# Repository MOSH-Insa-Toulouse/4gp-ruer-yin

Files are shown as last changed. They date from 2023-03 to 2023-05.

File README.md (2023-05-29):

# 22-23 4gp-ruer-yin

Ce projet s'inscrit dans l'UF **"I4GPMH21 - du capteur au banc de test en open source hardware"** en 4eme année département d'INSA Toulouse.
***

Ce projet sert à caractériser la résistance des capteurs graphites sous différentes conditions de déformation. Une application de déformation change la distance moyenne des particules de graphite. En effet, la conductivité de la couche graphite dépende vachement de cette distance moyenne et donc la déformation. En pratique, on applique un contraint et déposer le capteur sur les semis sphères pour caractériser les diffèrent déformation. L’ordre de grandeur de ce capteur est 100Mohm. Il n’est pas usuel. Par exemple il est hors la gamme de mesure des multimètres commerciaux. Donc il est essentiel dans ce projet de planifier et de fabriquer un circuit PCB qu’il nous permettre de mesurer cette résistance. De plus, il est aussi intéressant d’élaborer un système de communication pour communiquer les données avec notre téléphone Android avec Bluetooth. 
***  
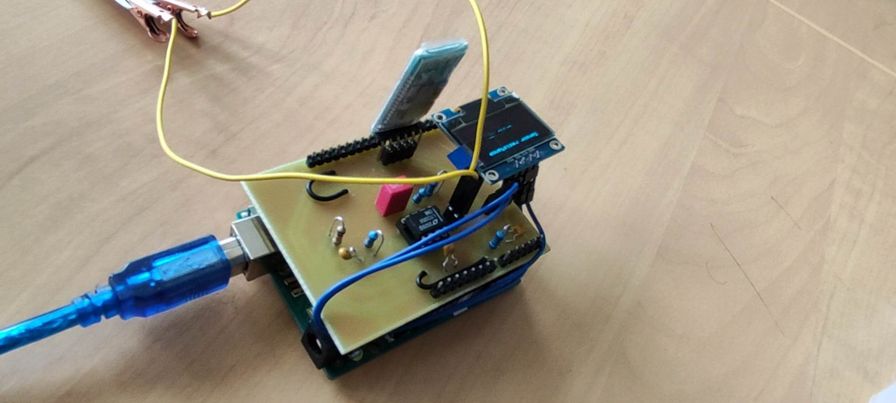
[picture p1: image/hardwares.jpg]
hardware

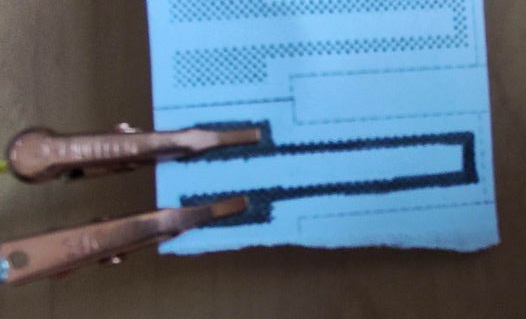
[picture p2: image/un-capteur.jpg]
capteur

## Table de matière
* [1. Liverables et matériels](#PremiereSection)
* [2. Simulation LTSPICE](#SixiemeSection)
* [3. Réalisation Kicad et PCB](#DeuxiemeSection)
* [4. Code Arduino](#TroisemeSection)
* [5. (Application MIT app inventor)](#QuartiemeSection)
* [6. (Banc de test)](#CinqiemeSection)
## 1. Liverables et matériels 
***
Les liverables principaux sont: 
* Un sheild PCB de module Arduino Uno au dessus on a intégré un circuit d'amplificateur, un OLED et un module Bluetooth.
* Un application Android exploré avec MIT app inventor. Cet app sert à communiquer en temp relle avec le module d'Arduino des valeurs de resistance et les afficher. 
* Un script d'Arduino permettant de calculer en temps relle du valeur de resistance, communiquer ce valeur avec l'application mentionné au dessus et l'afficher sur l'écran OLED
* Un datasheet contenant tous les caratérisation du capteur. 

Les matériels nécessaires sont:
* Un carte PCB de module Arduino Uno
* Un module Bluetooth HC-05
* Un écran OLED
* Un amplificateur opérationnel LTC1050  
* Deux condensateurs de 100 nF  
* Un condensateur de 100 µF 
* Deux résistances de 100 KOhms  
* Une résistance de 10 KOhms  
* Deux résistances de 1 KOhm  
* Un papier dessiné d'un trace de crayon imposé
## 2. Simulation LTSpice
La capteur graphite a une l'ordre de grandeur de 100MOhm. Le voltage maximun d'Arduino est 5V. Il est donc difficile de mesure la valeur de capteur si on n'arrive pas à amplifier la signal. On a donc designé un circuit d'amplification pour avoir un facteur 100 du signal. Ensuite on peut calculer le valeur précise de la résistance. Voici l'image du circuit de LTSpice:
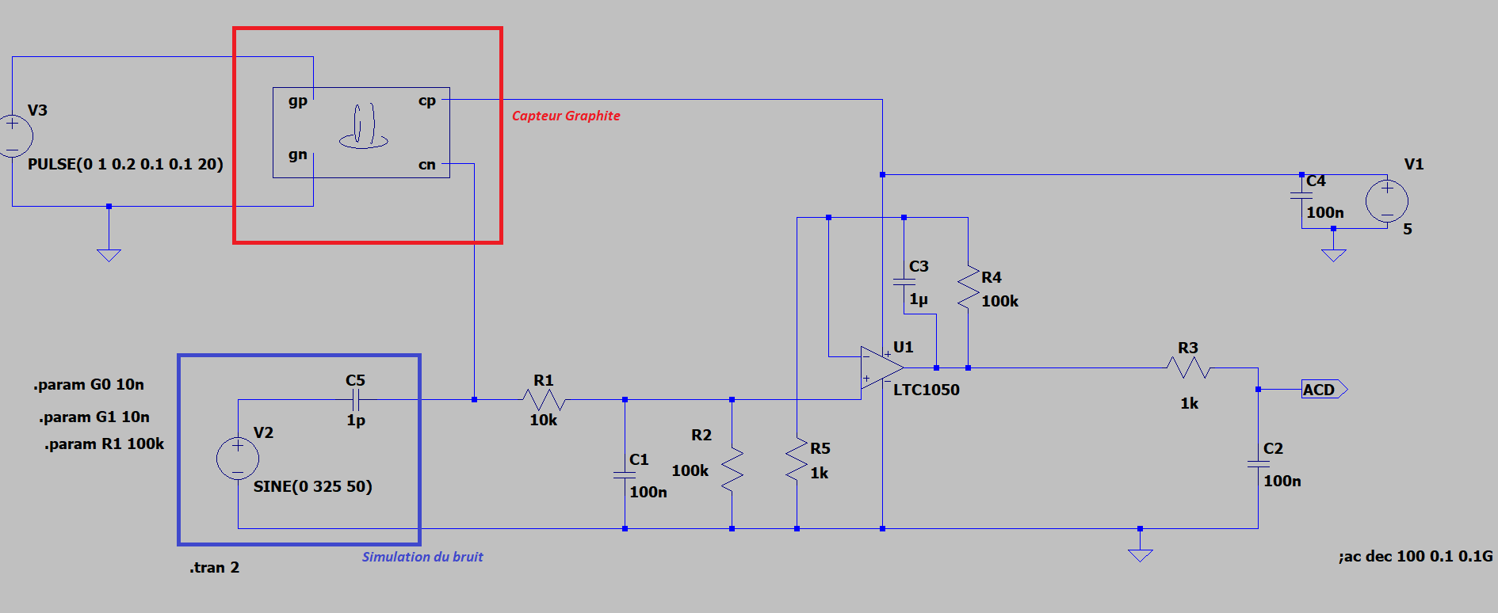
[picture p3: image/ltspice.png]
ltspice


## 3. Réalisation Kicad et PCB 
Pour designer un carte PCB où on peut intégrer les matériels mentionnés au dessus, il est nécessaire de utiliser kicad pour designer un circuit de conductant de cuivre et les composants soudés au dessus. Les détailes de ces composants et de la cirtuit sont visibles dans les images au dessous.  
* L'image des symboles:
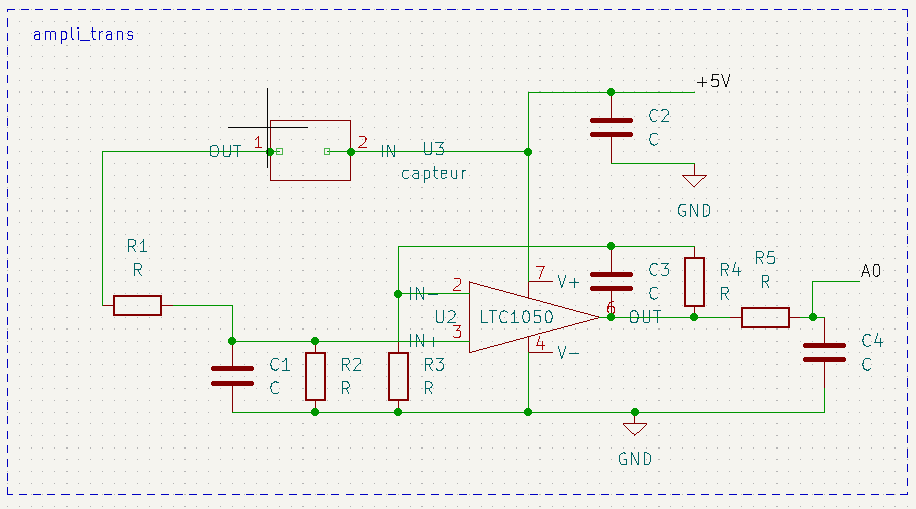
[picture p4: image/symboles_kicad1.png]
symbole1

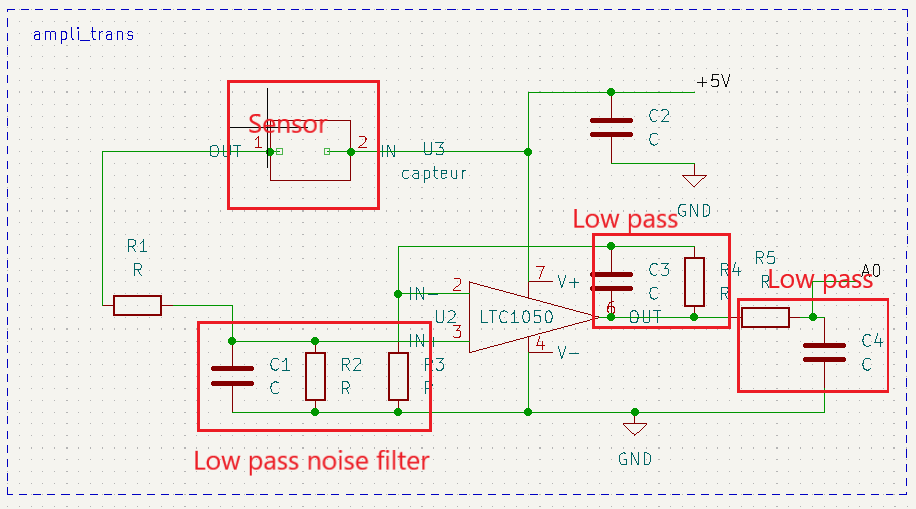
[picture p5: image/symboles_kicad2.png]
symbole2

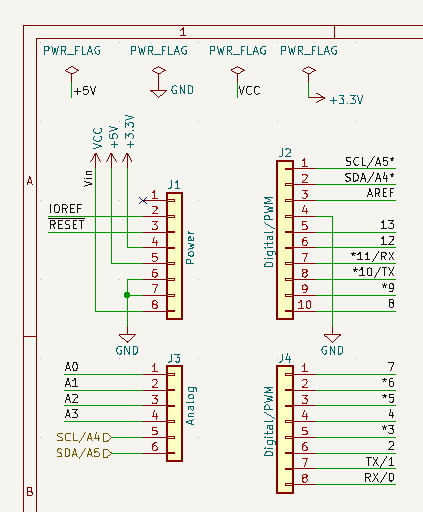
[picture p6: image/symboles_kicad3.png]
symbole3


* L'image du PCB et son image 3D
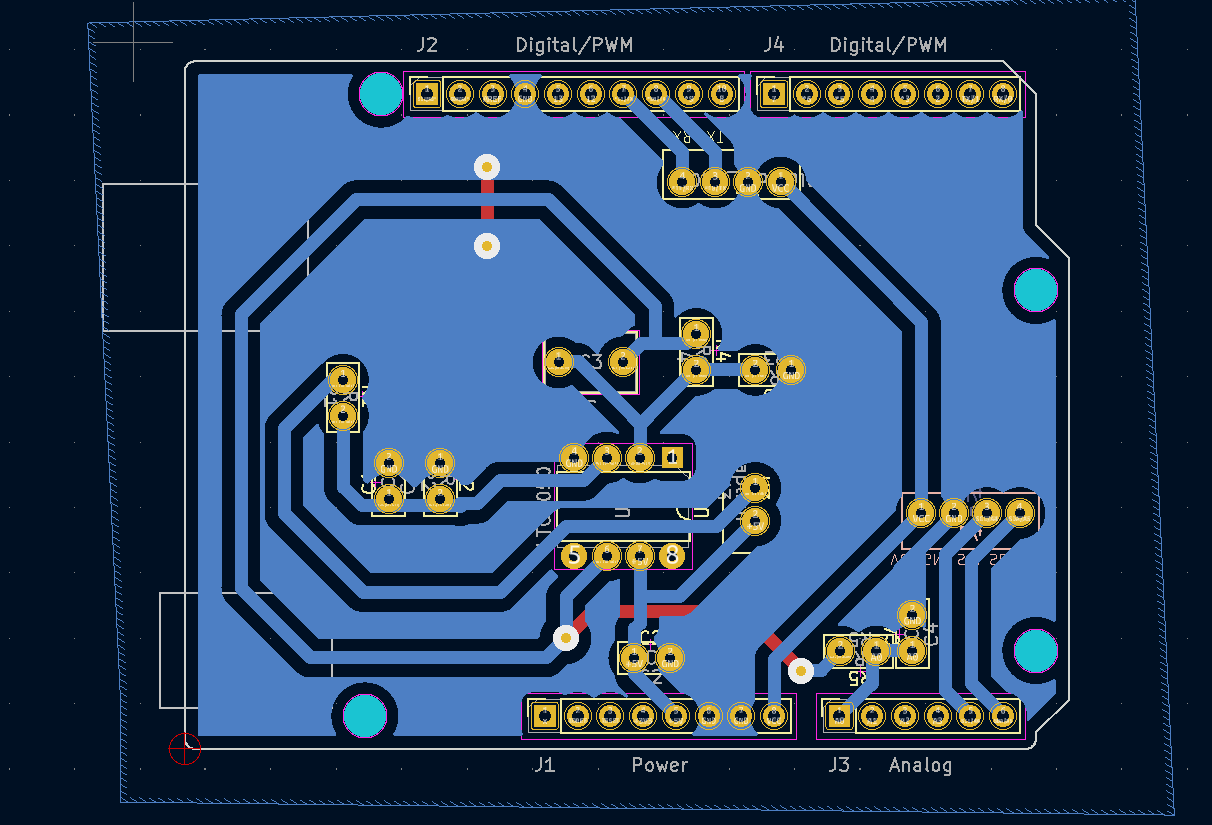
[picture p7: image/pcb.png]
pcb
 

Après les vérifications electroniques, nous avons envoyé le fichier d'imprimant à Madame Catherine Crouzet pour poursuivre un impression de PCB avec elle. Ce PCB est réalisé sur un plaquette epoxy. A la fin des procédés de photolitographie et de gravure chimique, l'impression du circuit est réalisé sur l'un de cette plaquette. Nous avons poursuive les perçages des trous pour intégrer les matériels et le soudage de ces matériels. Les trous on les 2 différents diamètres. Pour les trous du module Arduino Uno, le diametre est 1mm. Les trous de reste ont de diametre 0.8mm selon la consigne de Madame Catherine Crouzet.

## 4. Code Arduino 
Les objetifs de script d'arduino nommé [plz-work.ino](https://github.com/MOSH-Insa-Toulouse/4gp-ruer-yin/tree/main/Arduino/plz-work/plz-work) sont:
* mesurer le voltage en temp relle de la sortie du circuit (VA0)
* En déduire la valeur de résistance R du capteur graphite.
* Envoyer la valeur de tension mesuré sous 1 octect par le module de bluetooth.
* Afficher la valeur de résistance sur l'écran OLED.
Le code essentielle est effctivement les code de mesure et de calcule de valeur de résistance. Selon les simulations de LTSpice, on peut en deduit la resistance exact que nous aimerions de mesurer.

## 5. Application (MIT app inventor) 
Les objetifs de cet application est de communiquer en temp relle avec le module d'Arduino des valeurs de resistance et les afficher. 
La connection de bluetooth se réalise par trois bloc de "when". On affiche le liste d'adresse de bluetooth dans le mémoire de téléphone. Puis on pourra sélectionner un adresse. Le téléphone est ensuite connecté à bluetooth. 
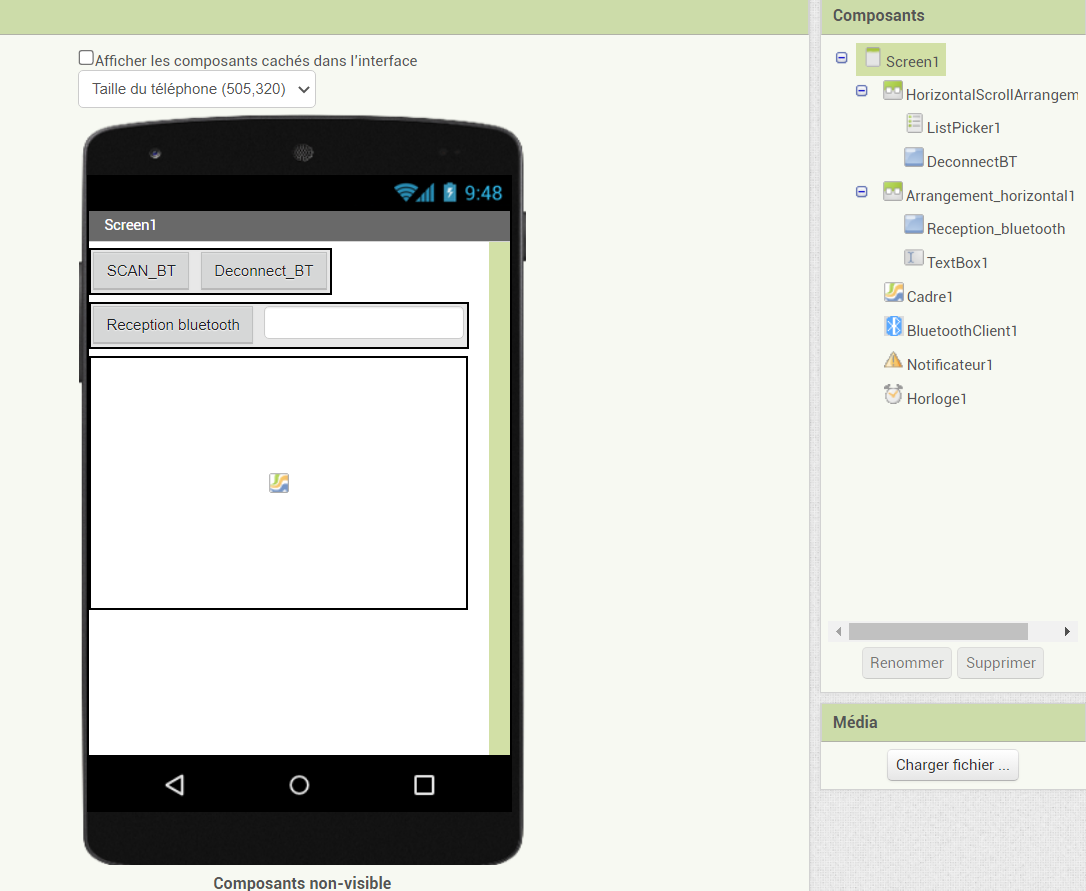
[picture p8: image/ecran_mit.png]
MIT


Le Bouton "Reception_bluetooth" sert à lancer le chronologe. Ensuite, l'application fait le calcule depuis un octet envoyé par le Bluetooth HC-05 en utilisant la simulation de LTspice. Dans le graphe, on trace le graphe en tracant tous les lignes entre tous les 2 point.   

## 6. Banc de test 
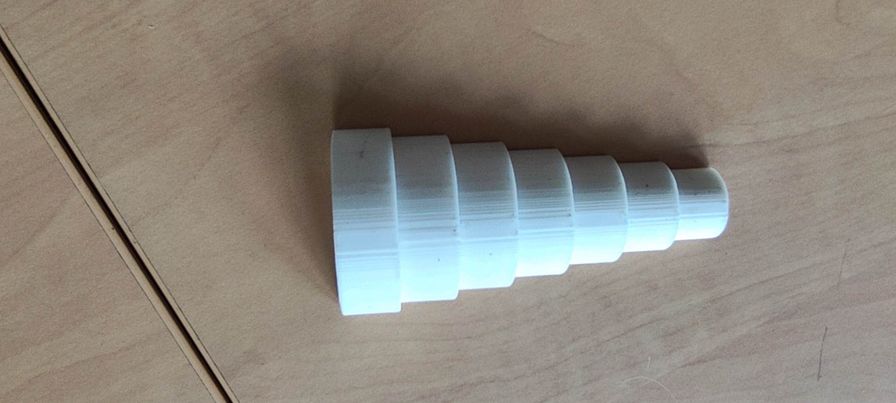
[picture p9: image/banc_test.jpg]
banc de test


Nous avons testé notre capteur graphite dans les différent angle de déformation. Ce dernier est caractériser par un banc de test dans l'image au dessus. Le banc de test est composé par les différents semi sphère de diamètre 5cm, 4.5cm, 4cm, 3.5cm, 3cm, 2.5cm, 2cm. Pendant le test, on colle le côté où il y a pas de graphite aux différent semi shère du banc de test et on fait le mesure du résistance. Ensuite on cherche la relation entre le déformation définit comme par le formule ε=D/(2*R)(où ε est la déformation, D est l'épaisseur du papier, R est la rayon de courbure) et la variation relative de (ΔR/R0).  
Nous avons décidé de faire les tests sur un graphite de 2H en applicant la seulement la tension. Il y a pas de mesure sous condition de compression car on a réalisé pendant les mesure que la forme de capteur graphite n'est pas réversible. Premièrement, on peut très facilement dépasser le limite élastique du papier. Deuxièmement, même si on ne change pas la forme de ce papier, la résistance n'est souvent pas réversible. En conséquence, on a choisit de faire le mesure seulment sur la tension pour chaque échantillon. Les résultat sont montré dans le fichier Datasheet.pdf.
Le résultat montre une relation linéaire entre la déformation et la variation relative de la résistance de capteur. On peut déduit l'angle de déformation  depuis un résistance mesurée. 

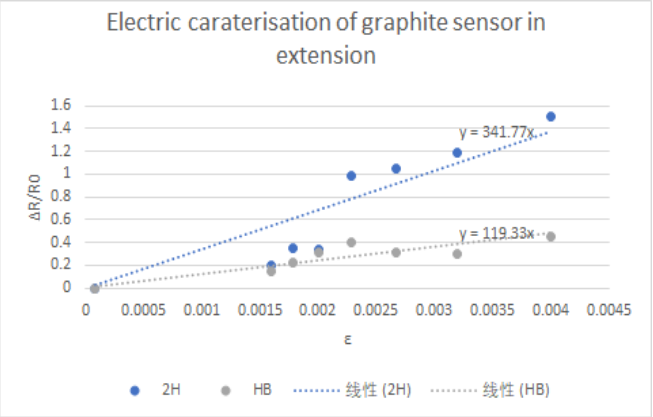
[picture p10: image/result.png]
result


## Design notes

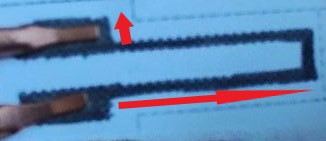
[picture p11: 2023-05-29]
image/344186423_743219774252609_5498657226306865498_o.jpg

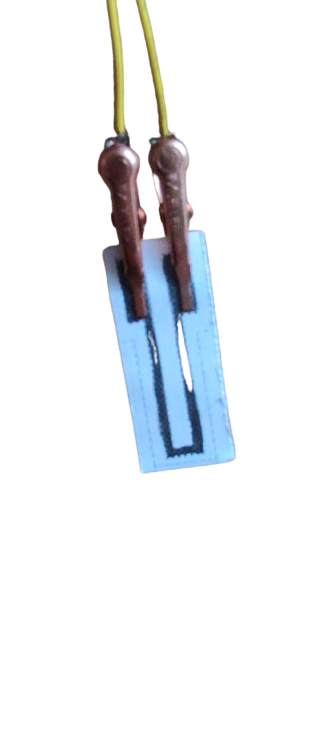
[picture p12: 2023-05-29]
image/344304782_1337325953871078_4266992527923061685_n-removebg-preview.png

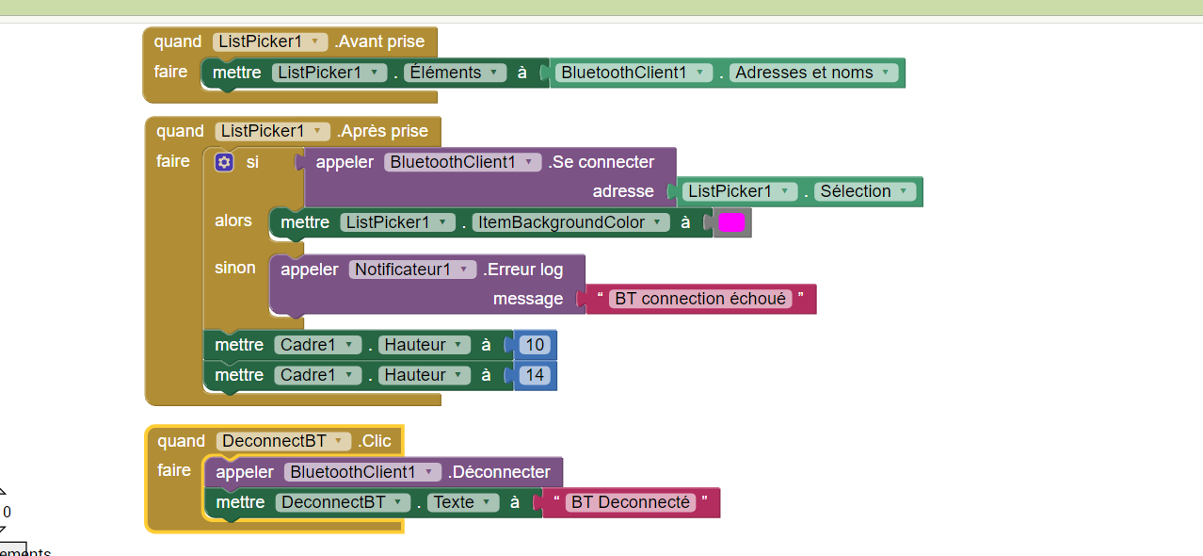
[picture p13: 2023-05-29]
image/MIT App Inventor 2 - Google Chrome 2023_5_11 22_43_18.png

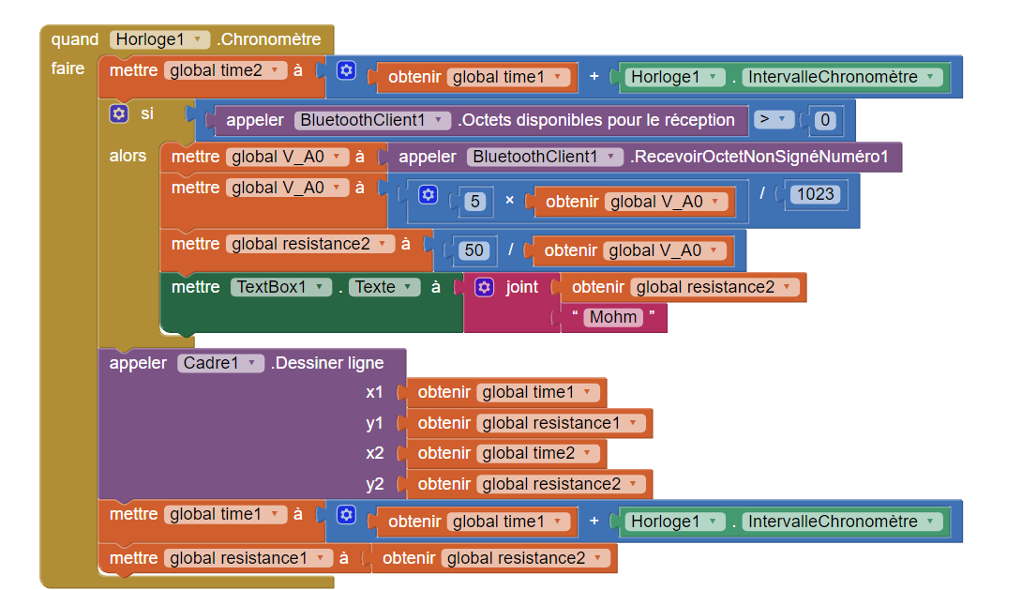
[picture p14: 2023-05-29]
image/MIT App Inventor 2 - Google Chrome 2023_5_12 16_00_10.png

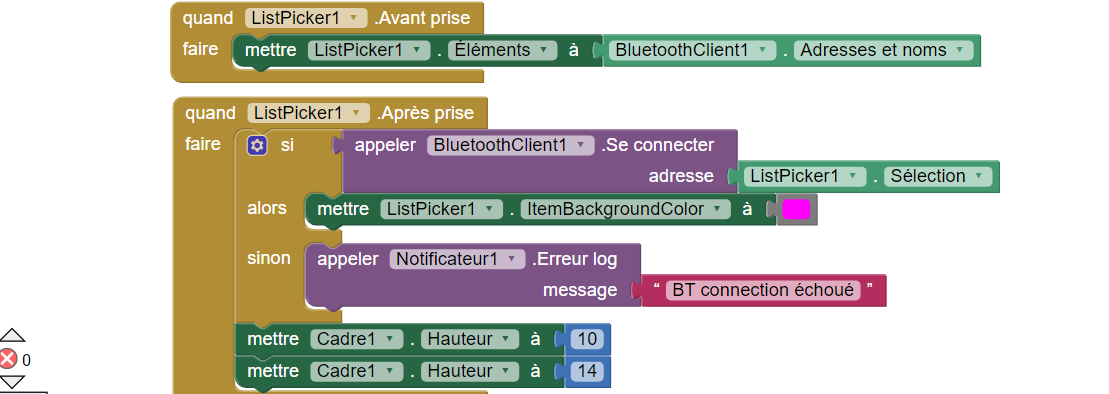
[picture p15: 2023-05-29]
image/MIT App Inventor 2 - Google Chrome 2023_5_11 22_40_17.png

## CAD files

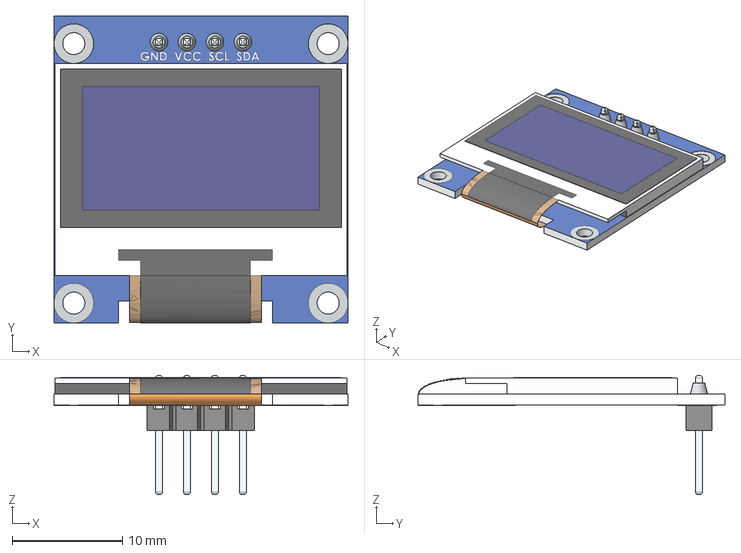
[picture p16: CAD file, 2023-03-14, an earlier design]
pcb_capteur_graphite_V2/mod3D/display-oled-ssd1306-de-0-96-1.snapshot.6/OLED-128x64-0.96.step
26.7 x 27.9 x 10.8 mm

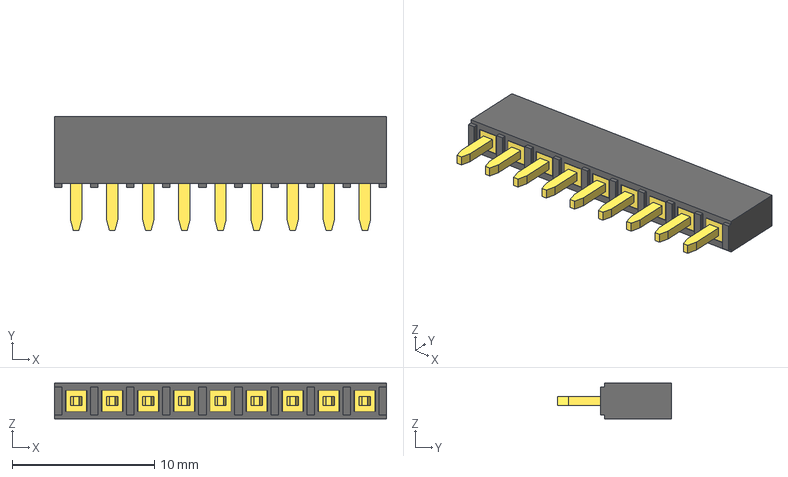
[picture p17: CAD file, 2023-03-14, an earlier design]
pcb_capteur_graphite_V2/mod3D/pin_header/9-Pin Header - Female - 2.54mm.step
23.4 x 8.00 x 2.50 mm

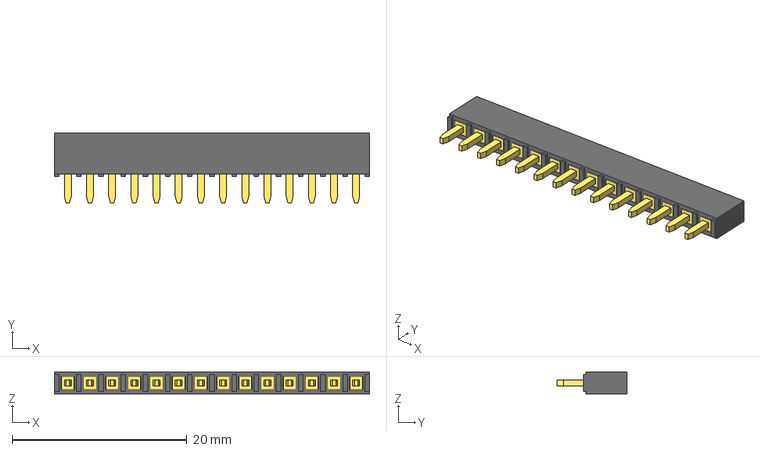
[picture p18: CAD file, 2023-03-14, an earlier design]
pcb_capteur_graphite_V2/mod3D/pin_header/14-Pin Header - Female - 2.54mm.step
36.1 x 8.00 x 2.50 mm

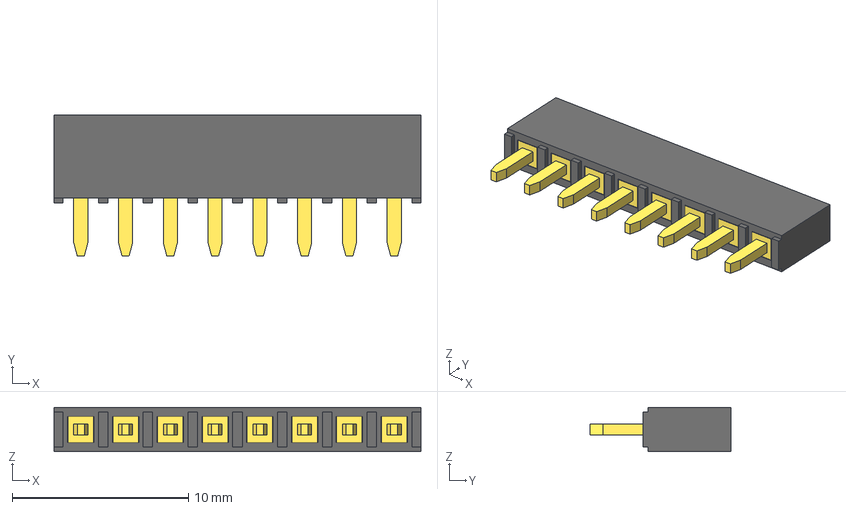
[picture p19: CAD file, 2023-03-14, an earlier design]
pcb_capteur_graphite_V2/mod3D/pin_header/8-Pin Header - Female - 2.54mm.step
20.8 x 8.00 x 2.50 mm

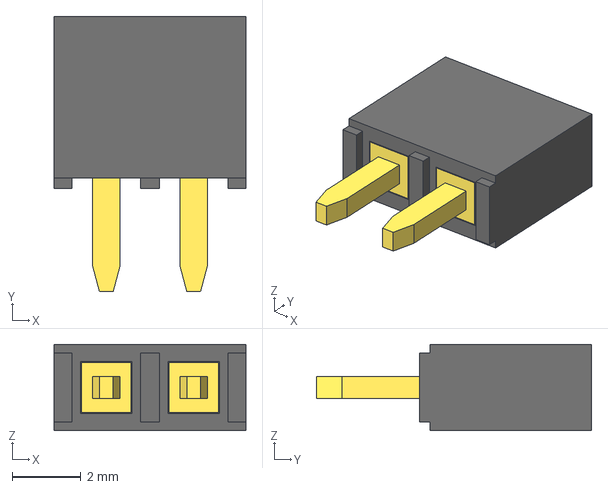
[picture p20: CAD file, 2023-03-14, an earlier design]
pcb_capteur_graphite_V2/mod3D/pin_header/2-Pin Header - Female - 2.54mm.step
5.58 x 8.00 x 2.50 mm

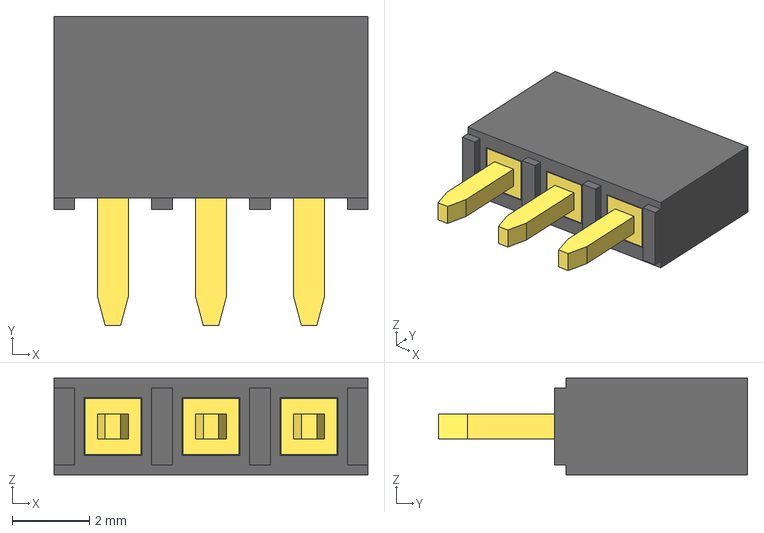
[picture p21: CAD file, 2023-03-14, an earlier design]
pcb_capteur_graphite_V2/mod3D/pin_header/3-Pin Header - Female - 2.54mm.step
8.12 x 8.00 x 2.50 mm

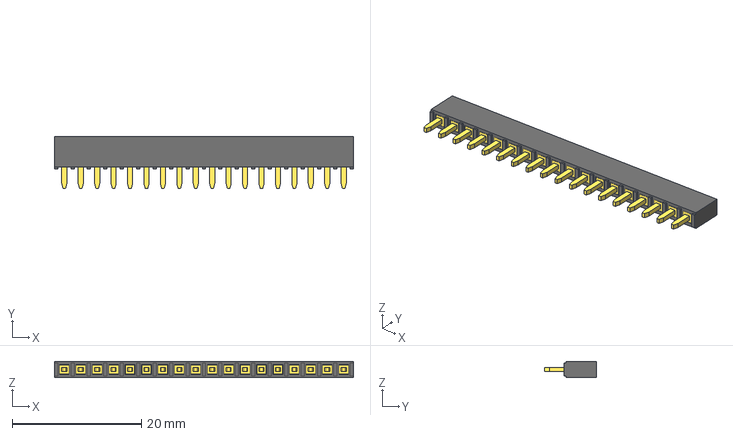
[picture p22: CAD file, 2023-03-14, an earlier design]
pcb_capteur_graphite_V2/mod3D/pin_header/18-Pin Header - Female - 2.54mm.step
46.2 x 8.00 x 2.50 mm

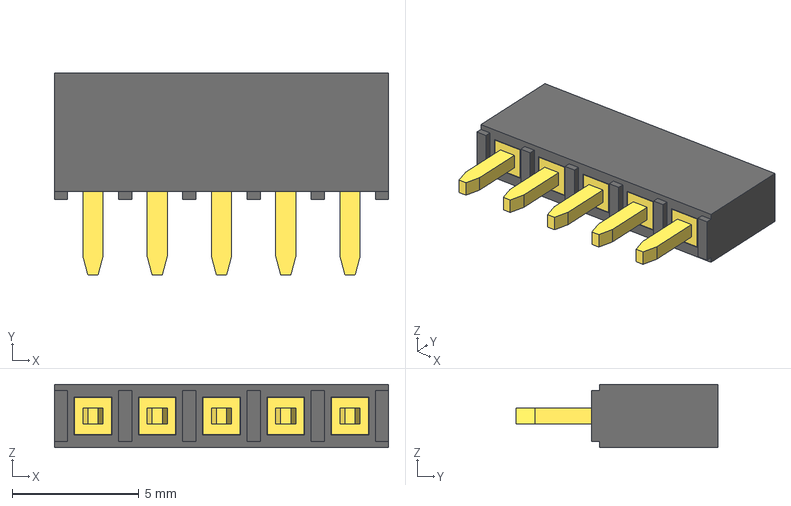
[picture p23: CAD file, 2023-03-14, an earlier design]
pcb_capteur_graphite_V2/mod3D/pin_header/5-Pin Header - Female - 2.54mm.step
13.2 x 8.00 x 2.50 mm

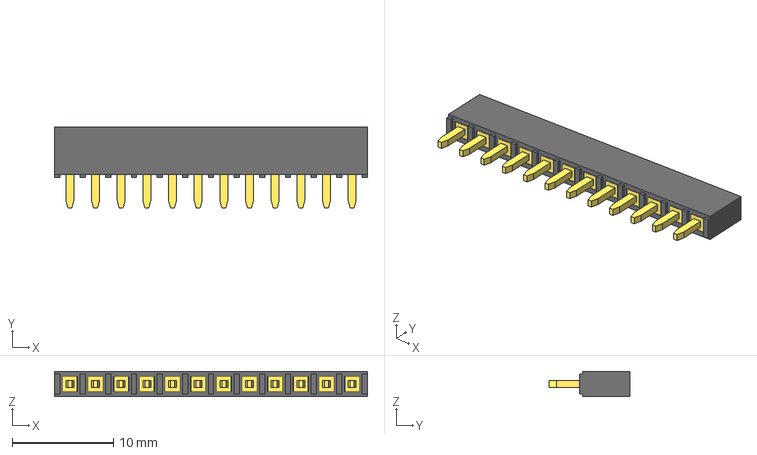
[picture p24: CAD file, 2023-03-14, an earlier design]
pcb_capteur_graphite_V2/mod3D/pin_header/12-Pin Header - Female - 2.54mm.step
31.0 x 8.00 x 2.50 mm

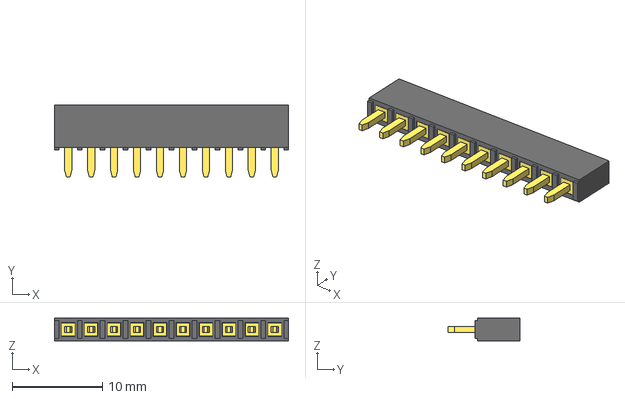
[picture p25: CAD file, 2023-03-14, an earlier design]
pcb_capteur_graphite_V2/mod3D/pin_header/10-Pin Header - Female - 2.54mm.step
25.9 x 8.00 x 2.50 mm

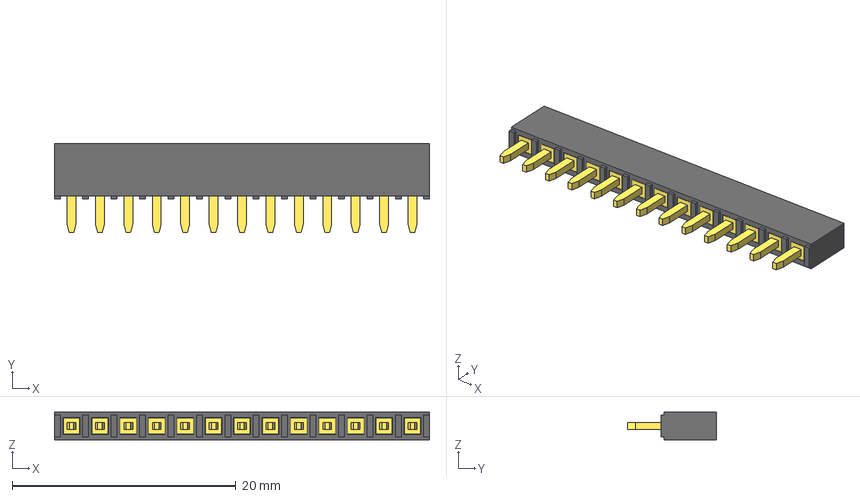
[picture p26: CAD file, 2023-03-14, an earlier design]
pcb_capteur_graphite_V2/mod3D/pin_header/13-Pin Header - Female - 2.54mm.step
33.5 x 8.00 x 2.50 mm

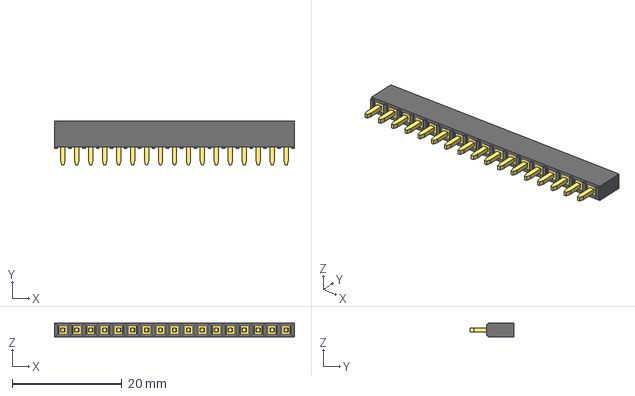
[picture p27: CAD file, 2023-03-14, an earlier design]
pcb_capteur_graphite_V2/mod3D/pin_header/17-Pin Header - Female - 2.54mm.step
43.7 x 8.00 x 2.50 mm

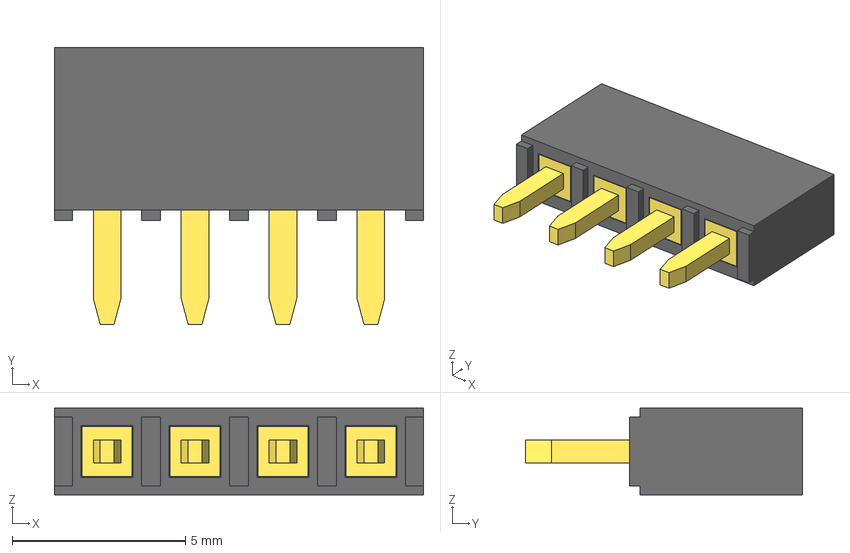
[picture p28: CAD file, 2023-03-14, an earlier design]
pcb_capteur_graphite_V2/mod3D/pin_header/4-Pin Header - Female - 2.54mm.step
10.7 x 8.00 x 2.50 mm

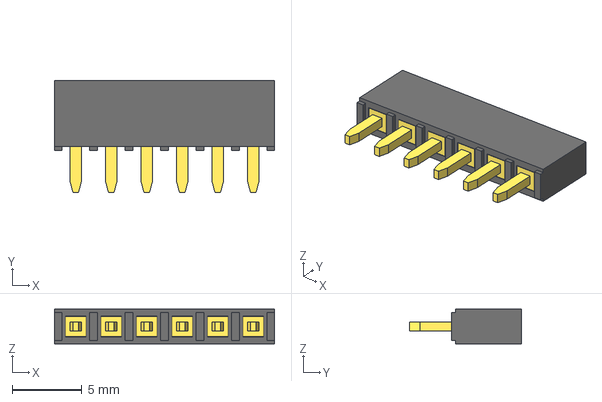
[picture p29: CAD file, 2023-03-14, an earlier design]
pcb_capteur_graphite_V2/mod3D/pin_header/6-Pin Header - Female - 2.54mm.step
15.7 x 8.00 x 2.50 mm

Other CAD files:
pcb_capteur_graphite_V2/mod3D/pin_header/11-Pin Header - Female - 2.54mm.step
pcb_capteur_graphite_V2/mod3D/pin_header/7-Pin Header - Female - 2.54mm.step
pcb_capteur_graphite_V2/mod3D/pin_header/15-Pin Header - Female - 2.54mm.step
pcb_capteur_graphite_V2/mod3D/pin_header/16-Pin Header - Female - 2.54mm.step
pcb_capteur_graphite_V2/mod3D/pin_header/19-Pin Header - Female - 2.54mm.step
pcb_capteur_graphite_V2/mod3D/pin_header/20-Pin Header - Female - 2.54mm.step

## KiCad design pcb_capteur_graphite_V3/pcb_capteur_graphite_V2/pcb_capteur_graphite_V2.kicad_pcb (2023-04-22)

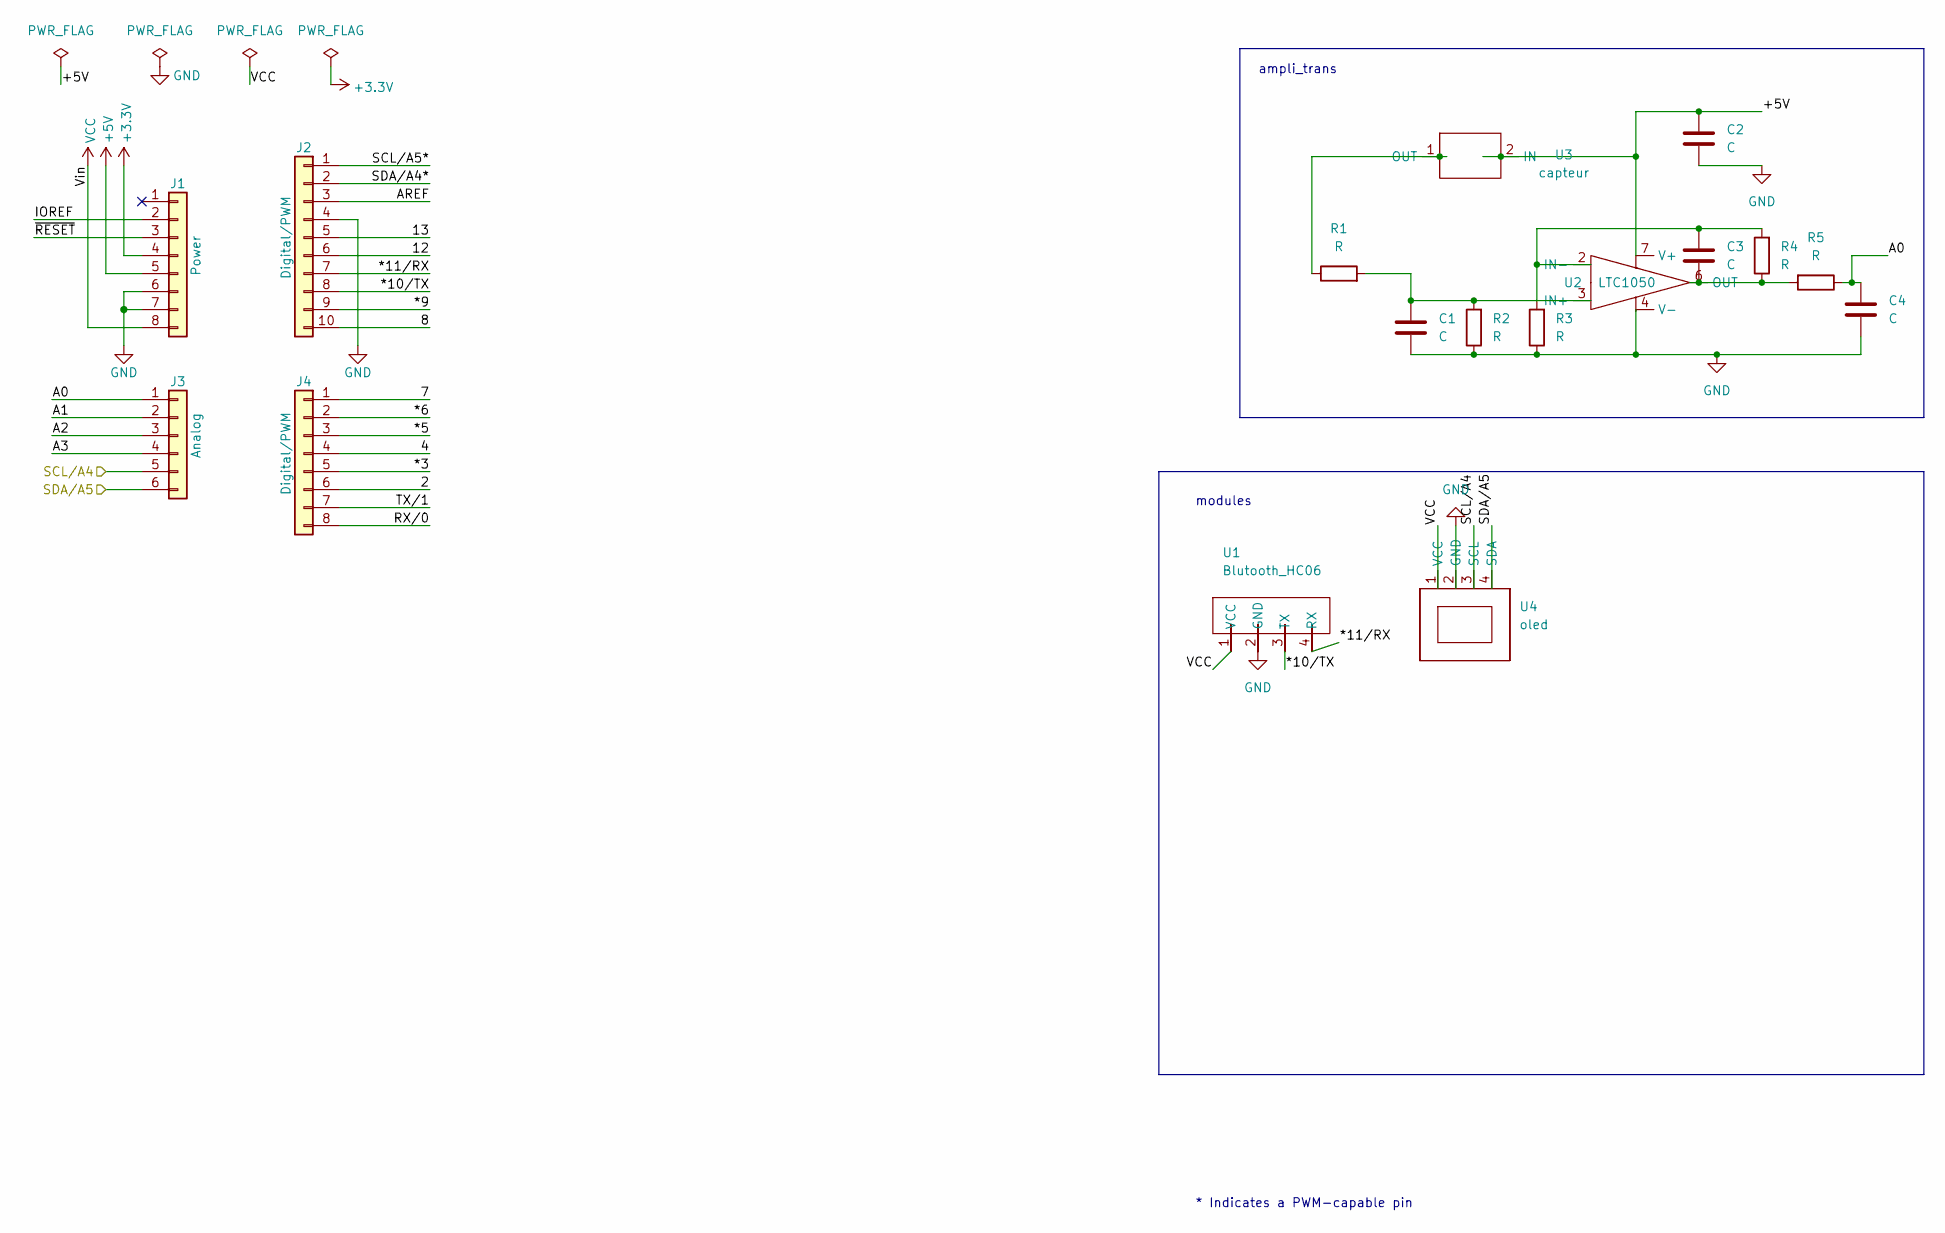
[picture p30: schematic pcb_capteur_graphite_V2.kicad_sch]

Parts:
C1, C2, C4: C; Conductance
C3: C; C_Rect_L7.0mm_W4.5mm_P5.00mm
J1: Power; PinSocket_1x08_P2.54mm_Vertical
J2: Digital/PWM; PinSocket_1x10_P2.54mm_Vertical
J3: Analog; PinSocket_1x06_P2.54mm_Vertical
J4: Digital/PWM; PinSocket_1x08_P2.54mm_Vertical
R1, R2, R3, R4, R5: R; Resistor
U1: Blutooth_HC06; Bluetooth
U2: LTC1050; DIP-8_W7.62mm
U3: capteur
U4: oled; OLED

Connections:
+3V3: J1.4
+5V: C2.1, J1.5, U2.7 (V+), U3.2 (IN)
/2: J4.6
/4: J4.4
/7: J4.1
/8: J2.10
/12: J2.6
/13: J2.5
/*3: J4.5
/*5: J4.3
/*6: J4.2
/*9: J2.9
/*10/TX: J2.8, U1.3 (TX)
/*11/RX: J2.7, U1.4 (RX)
/A0: C4.1, J3.1, R5.1
/A1: J3.2
/A2: J3.3
/A3: J3.4
/AREF: J2.3
/IOREF: J1.2
/RX/0: J4.8
/SCL/A4: J3.5, U4.3 (SCL)
/SCL/A5*: J2.1
/SDA/A4*: J2.2
/SDA/A5: J3.6, U4.4 (SDA)
/TX/1: J4.7
/~RESET: J1.3
GND: C1.2, C2.2, C4.2, J1.6, J1.7, J2.4, R2.1, R3.1, U1.2 (GND), U2.4 (V-), U4.2 (GND)
unnamed: C1.1, R1.2, R2.2, U2.3 (IN+)
unnamed: C3.1, R3.2, R4.2, U2.2 (IN-)
unnamed: C3.2, R4.1, R5.2, U2.6 (OUT)
unnamed: R1.1, U3.1 (OUT)
VCC: J1.8, U1.1 (VCC), U4.1 (VCC)

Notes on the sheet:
ampli_trans
modules
* Indicates a PWM-capable pin

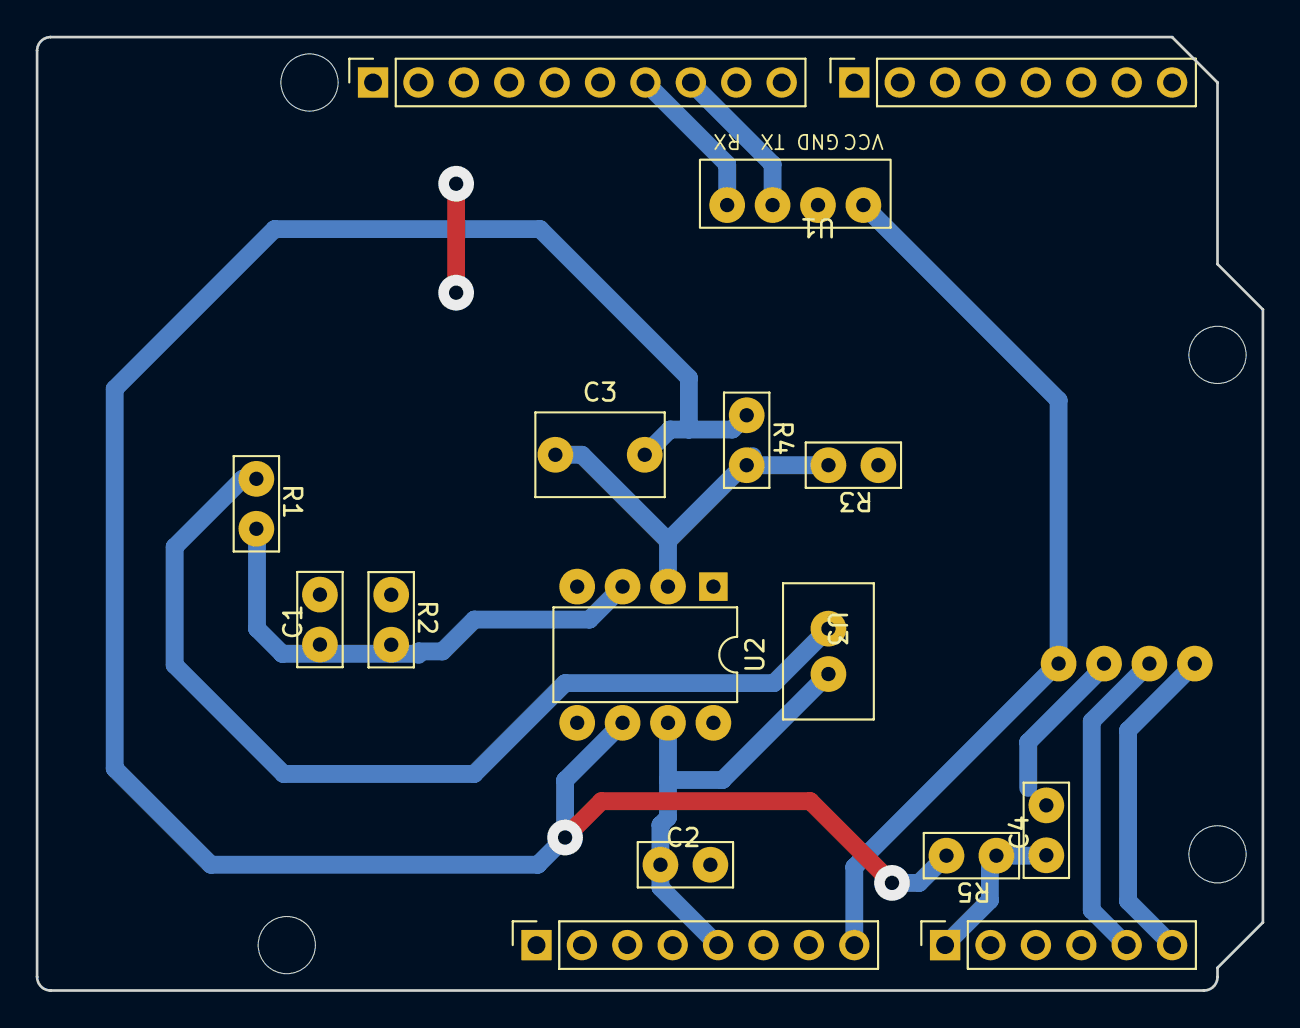
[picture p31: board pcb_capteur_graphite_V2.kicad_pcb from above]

Board: 2 copper layers, 68.6 x 53.3 mm, 21 parts (1 on the bottom side), 12 nets.

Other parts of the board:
MH1, MH2, MH3, MH4: MountingHole_3.2mm

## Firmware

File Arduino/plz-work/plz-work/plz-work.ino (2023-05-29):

#include <Adafruit_SSD1306.h>
#include <SoftwareSerial.h>
#define nombreDePixelsEnLargeur 128         // Taille de l'écran OLED, en pixel, au niveau de sa largeur
#define nombreDePixelsEnHauteur 64          // Taille de l'écran OLED, en pixel, au niveau de sa hauteur

#define x 128         // Taille de l'écran OLED, en pixel, au niveau de sa largeur
#define y 64          // Taille de l'écran OLED, en pixel, au niveau de sa hauteur

#define brocheResetOLED         -1          // Reset de l'OLED partagé avec l'Arduino (d'où la valeur à -1, et non un numéro de pin)
#define adresseI2CecranOLED     0x3C        // Adresse de "mon" écran OLED sur le bus i2c (généralement égal à 0x3C ou 0x3D)
#define rxPin 10 //Broche 11 en tant que RX, à raccorder sur TX du HC-05
#define txPin 11 //Broche 10 en tant que RX, à raccorder sur TX du HC-05
#define baudrate 38400
SoftwareSerial mySerial(rxPin ,txPin); //Definition du software serial

float voltage_output;
float Rc;
float VBT;
int binary_voltage;
#define R1 100000.0
#define R2  1000.0  
#define R3  100000.0   
#define R4  10000.0 
#define R5  1000.0 
#define Vcc  5.0 
float calibre = 0.000001; 

Adafruit_SSD1306 ecranOLED(x, y, &Wire, brocheResetOLED);

void setup() {
  
  if(!ecranOLED.begin(SSD1306_SWITCHCAPVCC, adresseI2CecranOLED))
    while(1);    
  
  ecranOLED.clearDisplay();
  ecranOLED.setTextSize(1);
  ecranOLED.setTextColor(SSD1306_WHITE, SSD1306_BLACK);

  pinMode(rxPin,INPUT);
  pinMode(txPin,OUTPUT);

  mySerial.begin(baudrate);
  Serial.begin(9600);
  ecranOLED.setCursor(10,y/2);
  ecranOLED.print("Initialization...");
  ecranOLED.display(); 
  delay(1000);
  ecranOLED.clearDisplay();


}

void loop() {

//Calcul Resistance jauge
voltage_output = analogRead(A0);
binary_voltage = voltage_output;
voltage_output = 5*voltage_output/1023;
//Rc = 50/voltage_output;
Rc= ((R1*((R2+R3)/R2)*(Vcc/voltage_output))-R4-R1)*calibre;

// Bluetooth
//mySerial.println(i); 
mySerial.write(voltage_output/4);
VBT = analogRead(A3); //voltage de rxPin su
VBT = VBT*5/1023;
Serial.print(binary_voltage); 
Serial.println("V");
Serial.print(VBT); 
Serial.println("V");
Serial.print(Rc); 
Serial.println("Ohm");
     
  
//Affichage et saisie de texte


String display_prompt1 = String(voltage_output,1);
String display_prompt2 = String(Rc,1);

ecranOLED.setCursor(25,0);
ecranOLED.print("Voltage output");
ecranOLED.setCursor(x/2 - 20, 10);
ecranOLED.print(display_prompt1 + " V");

ecranOLED.setCursor(15,y/2);
ecranOLED.print("Sensor resistance");
ecranOLED.setCursor(x/2 - 20,y-20);
ecranOLED.print(display_prompt2 + " MOhm");

ecranOLED.display();  
delay(1000);
ecranOLED.clearDisplay();

}

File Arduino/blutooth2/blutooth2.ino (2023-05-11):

#include <SoftwareSerial.h>
#define rxPin 11 //Broche 11 en tant que RX, à raccorder sur TX du HC-05
#define txPin 10 //Broche 10 en tant que RX, à raccorder sur TX du HC-05
#define baudrate 38400
SoftwareSerial mySerial(rxPin ,txPin); //D�finition du software serial

void setup() {
  // put your setup code here, to run once:
  pinMode(rxPin,INPUT);
  pinMode(txPin,OUTPUT);
    
  mySerial.begin(baudrate);
  Serial.begin(baudrate);
}

void loop() {
  // put your main code here, to run repeatedly:
  int i = 0; 
  
  //when characters arrive over the serial port...

  while (Serial.available()) {
     do{
    i++;//Serial.read();
    delay(3);   
     }while (Serial.available() > 0);
     
     mySerial.println(i); 
     Serial.println(i); 
  }
  while (mySerial.available()) {
    Serial.print((char)mySerial.read());
  }
}

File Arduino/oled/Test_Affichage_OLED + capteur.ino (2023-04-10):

/*
  Fichier :       afficherTexteSsd1306.ino
  Description :   Affiche du texte de test, sur un écran OLED i2c de 128x64 pixels,
                  fonctionnant avec un contrôleur SSD1306
  Auteur :        Jérôme TOMSKI (https://passionelectronique.fr/)
  Créé le :       26.07.2021
*/

#include <Adafruit_SSD1306.h>

#define nombreDePixelsEnLargeur 128         // Taille de l'écran OLED, en pixel, au niveau de sa largeur
#define nombreDePixelsEnHauteur 64          // Taille de l'écran OLED, en pixel, au niveau de sa hauteur
#define brocheResetOLED         -1          // Reset de l'OLED partagé avec l'Arduino (d'où la valeur à -1, et non un numéro de pin)
#define adresseI2CecranOLED     0x3C        // Adresse de "mon" écran OLED sur le bus i2c (généralement égal à 0x3C ou 0x3D)
float voltage_output;
float Rc;

Adafruit_SSD1306 ecranOLED(nombreDePixelsEnLargeur, nombreDePixelsEnHauteur, &Wire, brocheResetOLED);

void setup() {

  // Initialisation de l'écran OLED
  if(!ecranOLED.begin(SSD1306_SWITCHCAPVCC, adresseI2CecranOLED))
    while(1);                               // Arrêt du programme (boucle infinie) si échec d'initialisation

  // *************************************************************************
  // Affichage de 3 écrans successifs, avec zoom sur police x1, puis x2, et x3
  // *************************************************************************
  for(byte tailleDeCaractere=1; tailleDeCaractere <=3; tailleDeCaractere++) {
    boolean bCouleurInverse = false;
    ecranOLED.clearDisplay();                                   // Effaçage de l'intégralité du buffer
    ecranOLED.setTextSize(tailleDeCaractere);                   // Taille des caractères (1:1, puis 2:1, puis 3:1)
    ecranOLED.setCursor(0, 0);                                  // Déplacement du curseur en position (0,0), c'est à dire dans l'angle supérieur gauche

    // ***********************************************************************
    // Affichage de 8 lignes à couleurs alternées, dans chaque écran successif
    // ***********************************************************************
    /*
    for(byte numeroDeLigne=1; numeroDeLigne<=8; numeroDeLigne++) {
      if(bCouleurInverse)
        ecranOLED.setTextColor(SSD1306_BLACK, SSD1306_WHITE);   // Couleur du texte, et couleur du fond
      else
        ecranOLED.setTextColor(SSD1306_WHITE);                  // Affichage du texte en "blanc" (avec la couleur principale, en fait, car l'écran monochrome peut être coloré)
      ecranOLED.print("KILL BILL ");
      ecranOLED.println(numeroDeLigne);
      bCouleurInverse = !bCouleurInverse;
    }
    ecranOLED.display();                            // Transfert le buffer à l'écran
    delay(2000);
    */
  }
}

void loop() {
  // récupération du signal
  voltage_output = analogRead(A0);
 voltage_output = 5*voltage_output/1023;
 Rc = 50/voltage_output;
 /*
 Serial.print("ADC vaut :");
 Serial.print(voltage_output);
 Serial.println("V");
 Serial.print("Rc vaut :");
 Serial.print(Rc);
 Serial.println(" Mohms");
 delay(1000);
 */
// je n'afficher qu'un ligne
for(byte numeroDeLigne=1; numeroDeLigne<=1; numeroDeLigne++) {
      if(bCouleurInverse)
        ecranOLED.setTextColor(SSD1306_BLACK, SSD1306_WHITE);   // Couleur du texte, et couleur du fond
      else
        ecranOLED.setTextColor(SSD1306_WHITE);                  // Affichage du texte en "blanc" (avec la couleur principale, en fait, car l'écran monochrome peut être coloré)
      ecranOLED.print("KILL BILL ");
      ecranOLED.println(numeroDeLigne);
      bCouleurInverse = !bCouleurInverse;
    }
    ecranOLED.display();                            // Transfert le buffer à l'écran
    delay(2000);
 
}

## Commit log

2023-03-14 gitignore added - pcb fini
    [10-Pin Header - Female - 2.54mm.step, 11-Pin Header - Female - 2.54mm.step, 12-Pin Header - Female - 2.54mm.step, 13-Pin Header - Female - 2.54mm.step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]
2023-04-10 Code Arduino
2023-04-22 version de circuit imprimé
    [pcb_capteur_graphite_V2.kicad_pcb, pcb_capteur_graphite_V2.kicad_sch]
2023-05-10 MAJ pcb
    [pcb_capteur_graphite_V2.kicad_pcb, pcb_capteur_graphite_V2.kicad_sch]
2023-05-15 plz peut envoyer les octets
2023-05-29 tous les images
